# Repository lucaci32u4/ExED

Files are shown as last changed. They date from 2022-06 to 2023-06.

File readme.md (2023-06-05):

# Extended Digital Electronics laboratory

This laboratory is intended to be used as teaching material for the 6th Digital Electronics laboratory in the Faculty of Computer Science, Politehnica University of Bucharest.

This laboratory material presents the functioning of a shift register, a ring counter and a phase-locked loop. The following applications can be built:

 * A semaphore-like appliance using a ring counter
 * A clock divider
 * Phase-locked loop used to correct the pulse width of a fixed-frequency input signal
 * Clock multiplier bult using the phase-locked loop and clock divider
 * Linear feedback shift register - a random number generator using the shift register and XOR gate

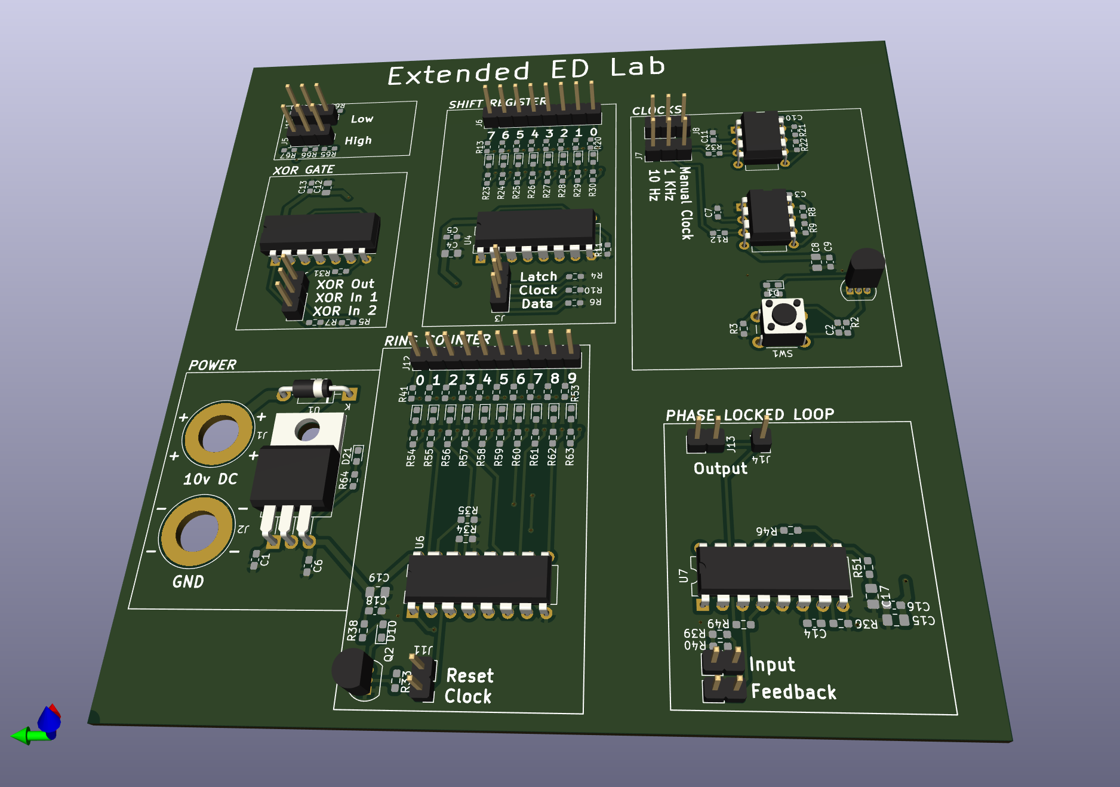
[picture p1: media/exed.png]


## Version v0.1

A batch of 10 boards v0.01 were built. Seven of them were populated and tested in field, while three were kept for archieval purposes.



After teaching the extended laboratory to two groups, the following observations can be made:

 * Replace the XOR gate with a XNOR gate to eliminate the need to seed the LFSR. A XNOR gate would allow it to be self-seeding.
 * There are missing traces near the shift registers that need to be drawn. This issue was fixed by hand using wire on the first batch
 * Remove R36 to allow a much more dynamic range for the PLL.
 * Add LED to all clock inputs to allow better observation of the circuit.
 * Add reverse-polarity protection.

These flaws are planned to be fixed in version v0.2.

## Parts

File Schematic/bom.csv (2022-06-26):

Id | Designator | Package | Quantity | Designation | Supplier and ref
1 | R60,R58,R28,R64,R56,R55,R30,R38,R24,R57,R26,R54,R59,R61,R27,R63,R29,R25,R62,R23,R1 | R_0603_1608Metric_Pad0.98x0.95mm_HandSolder | 21 | 330 | 2861870
2 | D22 | D_DO-41_SOD81_P10.16mm_Horizontal | 1 | 1N4001 | 1458986
3 | J11 | PinHeader_1x02_P2.54mm_Vertical | 1 | CounterControl
4 | U6 | DIP-16_W7.62mm | 1 | 4017 | 3006265
5 | R2,R33 | R_0603_1608Metric_Pad0.98x0.95mm_HandSolder | 2 | 1k | 9233385
6 | U1 | TO-220-3_Horizontal_TabDown | 1 | LM7805_TO220 | 9666095
7 | D4,D11,D5,D17,D2,D7,D13,D16,D1,D10,D18,D9,D8,D14,D19,D3,D15,D12,D6,D21,D20 | LED_0603_1608Metric_Pad1.05x0.95mm_HandSolder | 21 | LED | 2687486
8 | C17,C19,C4,C12,C15,C8 | C_0805_2012Metric_Pad1.18x1.45mm_HandSolder | 6 | 100n | 1414615
9 | U4 | DIP-16_W7.62mm | 1 | 74HC595 | 3120865
10 | J4 | PinHeader_1x03_P2.54mm_Vertical | 1 | XOR
11 | J7,J8 | PinHeader_1x03_P2.54mm_Vertical | 2 | Clocks
12 | R12,R32,R49,R31,R65,R16,R53,R18,R17,R42,R43,R52,R47,R68,R13,R41,R48,R66,R45,R14,R20,R15,R67,R50,R70,R44,R19,R69 | R_0603_1608Metric_Pad0.98x0.95mm_HandSolder | 28 | 100 | 9233253
13 | J3 | PinHeader_1x03_P2.54mm_Vertical | 1 | ShiftInput
14 | C13,C6,C1,C9,C11,C5,C16,C18,C2 | CP_Radial_D4.0mm_P2.00mm | 9 | 1u | 9452524 | changed to 0603 code 1658868
15 | U7 | DIP-16_W7.62mm | 1 | 4046 | 3123331
16 | U5,U2 | DIP-8_W7.62mm | 2 | NE555P | 3006909
17 | J12 | PinHeader_1x10_P2.54mm_Vertical | 1 | CounterOutput
18 | Q1,Q2 | TO-92_Inline | 2 | PN2222A | 1700711
19 | J14 | PinHeader_1x01_P2.54mm_Vertical | 1 | PLLOutput
20 | J15 | PinHeader_1x03_P2.54mm_Vertical | 1 | LogicLow
21 | J2 | Banana_Jack_1Pin | 1 | BananaMinus
22 | J1 | Banana_Jack_1Pin | 1 | BananaPlus
23 | J6 | PinHeader_1x08_P2.54mm_Vertical | 1 | ShiftOutput
24 | R51,R11,R6,R4,R7,R34,R40,R35,R39,R5,R10 | R_0603_1608Metric_Pad0.98x0.95mm_HandSolder | 11 | 10k | 2008360
25 | J10,J9 | PinHeader_1x02_P2.54mm_Vertical | 2 | PLLDivider
26 | C7,C3,C10 | C_1206_3216Metric_Pad1.33x1.80mm_HandSolder | 3 | 10n | 491202 | changed to 0603 code 722236
27 | J5 | PinHeader_1x03_P2.54mm_Vertical | 1 | LogicHigh
28 | SW1 | SW_PUSH_6mm | 1 | Manual
29 | U3 | DIP-14_W7.62mm | 1 | 74LS00 | 3120419
30 | J13 | PinHeader_1x02_P2.54mm_Vertical | 1 | PLLOutput
31 | R9,R22,R8,R21 | R_0603_1608Metric_Pad0.98x0.95mm_HandSolder | 4 | 47k | 1652881
32 | R46,R36 | R_0603_1608Metric_Pad0.98x0.95mm_HandSolder | 2 | 100k | 9233628
33 | R37 | R_0603_1608Metric_Pad0.98x0.95mm_HandSolder | 1 | 10M | 2446549
34 | C14 | C_0603_1608Metric_Pad1.08x0.95mm_HandSolder | 1 | 1nF | 1740627
35 | R3 | R_0603_1608Metric_Pad0.98x0.95mm_HandSolder | 1 | 500 |  | // TODO: replace with 330 ohm

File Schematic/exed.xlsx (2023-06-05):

Id | Designator | Footprint | Quantity | Designation | Supplier and ref
1 | R60,R58,R28,R64,R56,R55,R30,R38,R24,R57,R26,R54,R59,R61,R27,R63,R29,R1,R25,R62,R23 | R_0603_1608Metric_Pad0.98x0.95mm_HandSolder | 21 | 330
2 | D22 | D_DO-41_SOD81_P10.16mm_Horizontal | 1 | 1N4001
3 | J11 | PinHeader_1x02_P2.54mm_Vertical | 1 | CounterControl
4 | U6 | DIP-16_W7.62mm | 1 | 4017
5 | R2,R33 | R_0603_1608Metric_Pad0.98x0.95mm_HandSolder | 2 | 1k
6 | U1 | TO-220-3_Horizontal_TabDown | 1 | LM7805_TO220
7 | D4,D11,D5,D17,D2,D7,D13,D16,D1,D10,D18,D9,D8,D14,D19,D3,D15,D12,D6,D21,D20 | LED_0603_1608Metric_Pad1.05x0.95mm_HandSolder | 21 | LED
8 | C17,C19,C4,C12,C15,C8 | C_0805_2012Metric_Pad1.18x1.45mm_HandSolder | 6 | 100n
9 | U4 | DIP-16_W7.62mm | 1 | 74HC595
10 | J4 | PinHeader_1x03_P2.54mm_Vertical | 1 | XOR
11 | J7,J8 | PinHeader_1x03_P2.54mm_Vertical | 2 | Clocks
12 | R12,R32,R49,R31,R65,R16,R53,R18,R17,R42,R43,R52,R47,R68,R13,R41,R48,R66,R45,R14,R20,R15,R67,R50,R70,R44,R19,R69 | R_0603_1608Metric_Pad0.98x0.95mm_HandSolder | 28 | 100
13 | J3 | PinHeader_1x03_P2.54mm_Vertical | 1 | ShiftInput
14 | C13,C6,C1,C11,C5,C16,C18,C2,C9 | C_0603_1608Metric_Pad1.08x0.95mm_HandSolder | 9 | 1u
15 | U7 | DIP-16_W7.62mm | 1 | 4046
16 | U5,U2 | DIP-8_W7.62mm | 2 | NE555P
17 | J12 | PinHeader_1x10_P2.54mm_Vertical | 1 | CounterOutput
18 | Q1,Q2 | TO-92_Inline | 2 | PN2222A
19 | J14 | PinHeader_1x01_P2.54mm_Vertical | 1 | PLLOutput
20 | J15 | PinHeader_1x03_P2.54mm_Vertical | 1 | LogicLow
21 | J2 | Banana_Jack_1Pin | 1 | BananaMinus
22 | J1 | Banana_Jack_1Pin | 1 | BananaPlus
23 | J6 | PinHeader_1x08_P2.54mm_Vertical | 1 | ShiftOutput
24 | R51,R11,R6,R4,R7,R34,R40,R35,R39,R5,R10 | R_0603_1608Metric_Pad0.98x0.95mm_HandSolder | 11 | 10k
25 | J10,J9 | PinHeader_1x02_P2.54mm_Vertical | 2 | PLLDivider
26 | C7,C3,C10 | C_0603_1608Metric_Pad1.08x0.95mm_HandSolder | 3 | 10n
27 | J5 | PinHeader_1x03_P2.54mm_Vertical | 1 | LogicHigh
28 | SW1 | SW_PUSH_6mm | 1 | Manual
29 | U3 | DIP-14_W7.62mm | 1 | 74LS00
30 | J13 | PinHeader_1x02_P2.54mm_Vertical | 1 | PLLOutput
31 | R9,R22,R8,R21 | R_0603_1608Metric_Pad0.98x0.95mm_HandSolder | 4 | 47k
32 | R46,R36 | R_0603_1608Metric_Pad0.98x0.95mm_HandSolder | 2 | 100k
33 | R37 | R_0603_1608Metric_Pad0.98x0.95mm_HandSolder | 1 | 10M
34 | C14 | C_0603_1608Metric_Pad1.08x0.95mm_HandSolder | 1 | 1nF
35 | R3 | R_0603_1608Metric_Pad0.98x0.95mm_HandSolder | 1 | 500

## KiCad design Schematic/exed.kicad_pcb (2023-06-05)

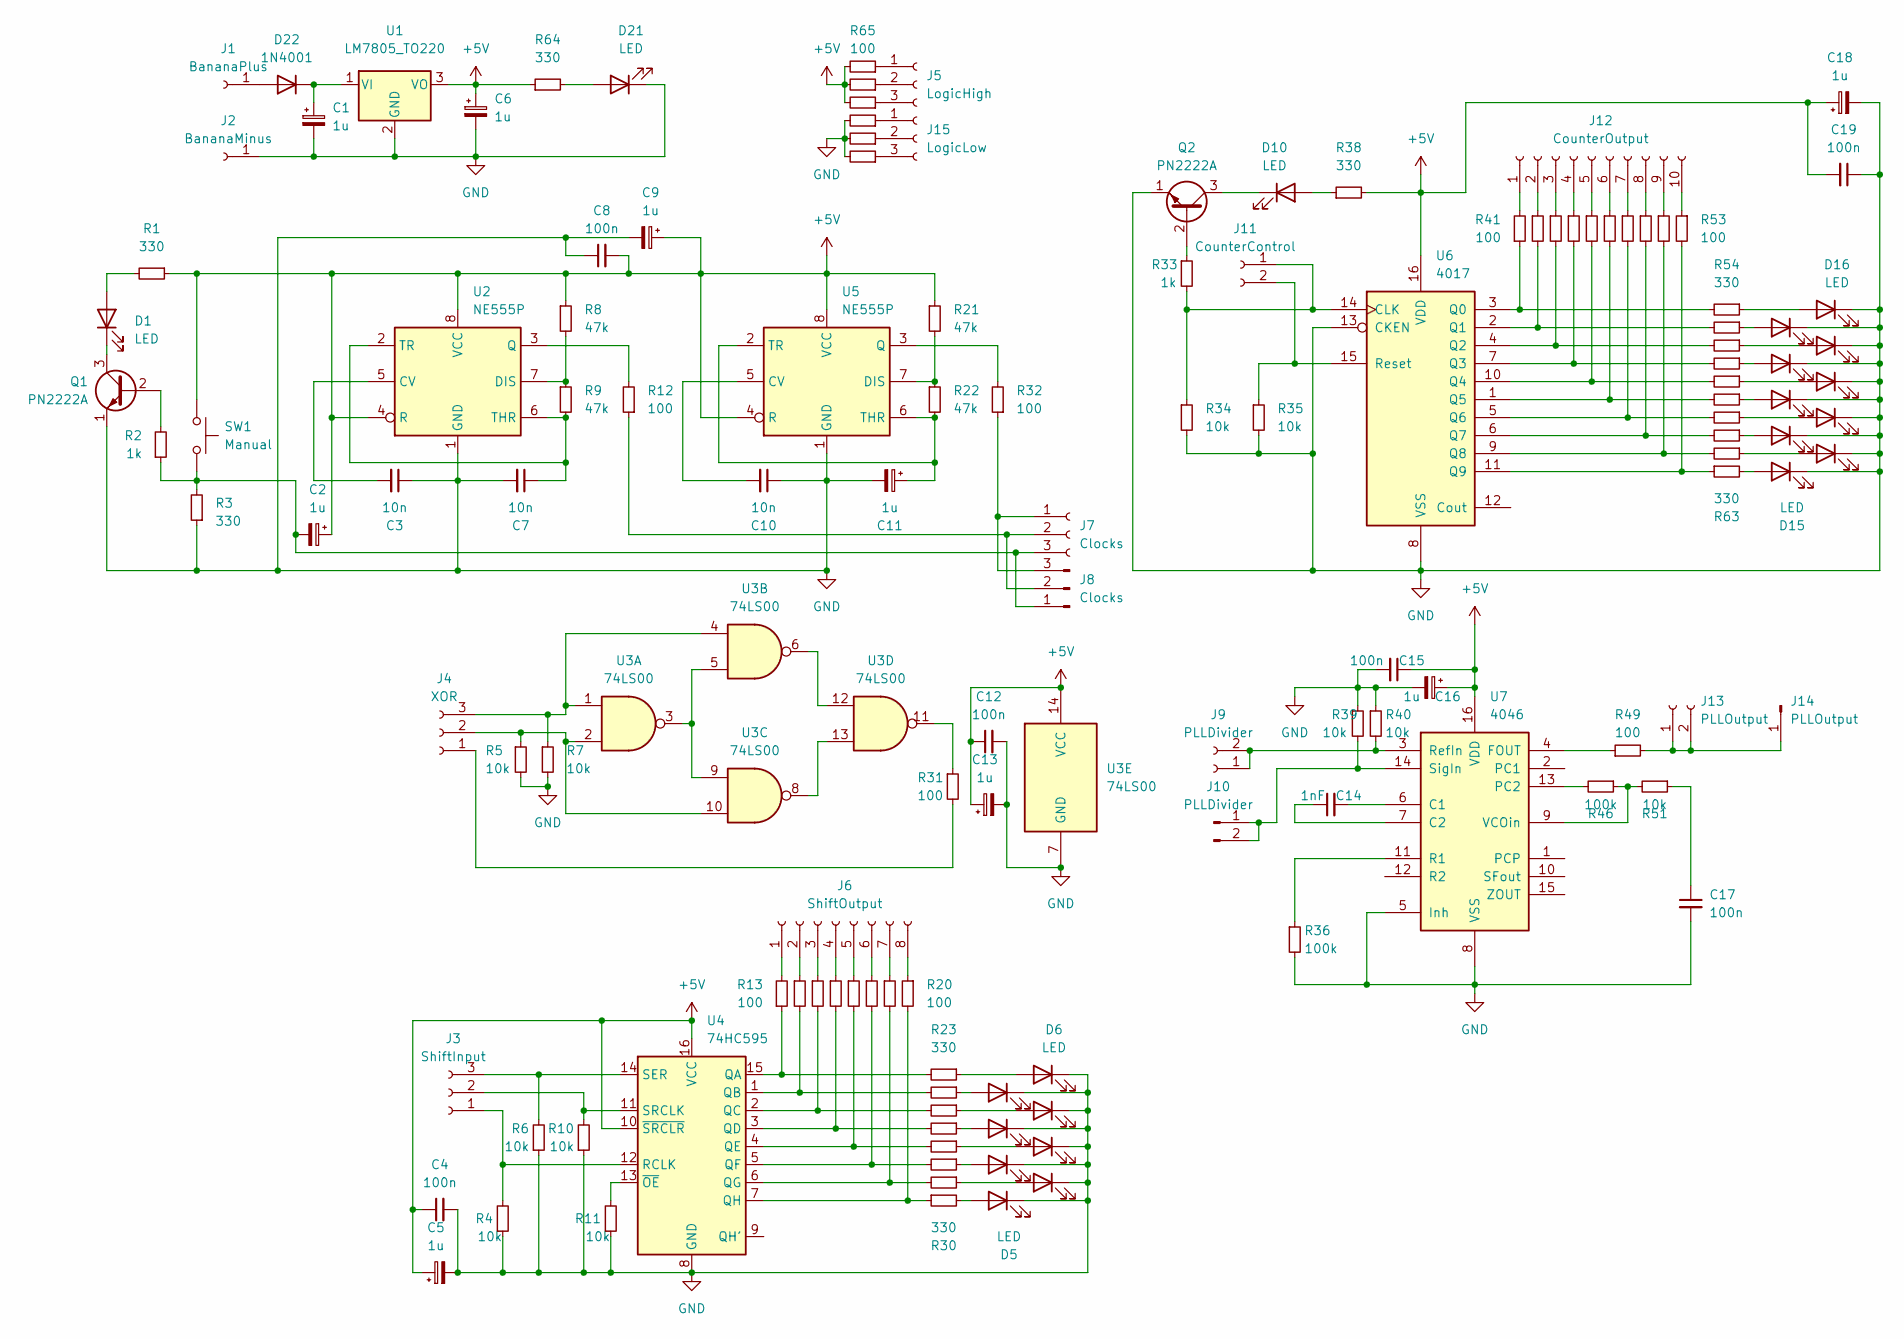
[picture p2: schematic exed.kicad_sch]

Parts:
C1, C2, C5, C6, C9, C11, C13, C16, C18: 1u; C_0603_1608Metric_Pad1.08x0.95mm_HandSolder
C3, C7, C10: 10n; C_0603_1608Metric_Pad1.08x0.95mm_HandSolder
C4, C8, C12, C15, C17, C19: 100n; C_0805_2012Metric_Pad1.18x1.45mm_HandSolder
C14: 1nF; C_0603_1608Metric_Pad1.08x0.95mm_HandSolder
D1, D2, D3, D4, D5, D6, D7, D8, D9, D10, D11, D12, D13, D14, D15, D16, D17, D18, D19, D20, D21: LED; LED_0603_1608Metric_Pad1.05x0.95mm_HandSolder
D22: 1N4001; D_DO-41_SOD81_P10.16mm_Horizontal
J1: BananaPlus; Banana_Jack_1Pin
J2: BananaMinus; Banana_Jack_1Pin
J3: ShiftInput; PinHeader_1x03_P2.54mm_Vertical
J4: XOR; PinHeader_1x03_P2.54mm_Vertical
J5: LogicHigh; PinHeader_1x03_P2.54mm_Vertical
J6: ShiftOutput; PinHeader_1x08_P2.54mm_Vertical
J7, J8: Clocks; PinHeader_1x03_P2.54mm_Vertical
J9, J10: PLLDivider; PinHeader_1x02_P2.54mm_Vertical
J11: CounterControl; PinHeader_1x02_P2.54mm_Vertical
J12: CounterOutput; PinHeader_1x10_P2.54mm_Vertical
J13: PLLOutput; PinHeader_1x02_P2.54mm_Vertical
J14: PLLOutput; PinHeader_1x01_P2.54mm_Vertical
J15: LogicLow; PinHeader_1x03_P2.54mm_Vertical
Q1, Q2: PN2222A; TO-92_Inline
R1, R3, R23, R24, R25, R26, R27, R28, R29, R30, R38, R54, R55, R56, R57, R58, R59, R60, R61, R62, R63, R64: 330; R_0603_1608Metric_Pad0.98x0.95mm_HandSolder
R2, R33: 1k; R_0603_1608Metric_Pad0.98x0.95mm_HandSolder
R4, R5, R6, R7, R10, R11, R34, R35, R39, R40, R51: 10k; R_0603_1608Metric_Pad0.98x0.95mm_HandSolder
R8, R9, R21, R22: 47k; R_0603_1608Metric_Pad0.98x0.95mm_HandSolder
R12, R13, R14, R15, R16, R17, R18, R19, R20, R31, R32, R41, R42, R43, R44, R45, R47, R48, R49, R50, R52, R53, R65, R66, R67, R68, R69, R70: 100; R_0603_1608Metric_Pad0.98x0.95mm_HandSolder
R36, R46: 100k; R_0603_1608Metric_Pad0.98x0.95mm_HandSolder
SW1: Manual; SW_PUSH_6mm
U1: LM7805_TO220; TO-220-3_Horizontal_TabDown
U2, U5: NE555P; DIP-8_W7.62mm
U3: 74LS00; DIP-14_W7.62mm
U4: 74HC595; DIP-16_W7.62mm
U6: 4017; DIP-16_W7.62mm
U7: 4046; DIP-16_W7.62mm

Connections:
+5V: C2.1, C4.1, C5.1, C6.1, C8.2, C9.1, C12.1, C13.1, C15.1, C16.1, C18.1, C19.2, R1.1, R8.1, R21.1, R38.2, R64.1, R65.2, R66.2, R67.2, SW1.1, U1.3 (VO), U2.4 (R), U2.8 (VCC), U3.14 (VCC), U4.10 (~SRCLR), U4.16 (VCC), U5.4 (R), U5.8 (VCC), U6.16 (VDD), U7.16 (VDD)
GND: C1.2, C3.1, C4.2, C5.2, C6.2, C7.2, C8.1, C9.2, C10.1, C11.2, C12.2, C13.2, C15.2, C16.2, C17.2, C18.2, C19.1, D2.1 (K), D3.1 (K), D4.1 (K), D5.1 (K), D6.1 (K), D7.1 (K), D8.1 (K), D9.1 (K), D11.1 (K), D12.1 (K), D13.1 (K), D14.1 (K), D15.1 (K), D16.1 (K), D17.1 (K), D18.1 (K), D19.1 (K), D20.1 (K), D21.1 (K), J2.1, Q1.1 (E), Q2.1 (E), R3.1, R4.1, R5.2, R6.1, R7.2, R10.1, R11.1, R34.2, R35.2, R36.2, R39.1, R40.1, R68.2, R69.2, R70.2, U1.2 (GND), U2.1 (GND), U3.7 (GND), U4.8 (GND), U5.1 (GND), U6.8 (VSS), U6.13 (CKEN), U7.5 (Inh), U7.8 (VSS)
unnamed: C17.1, R51.1
unnamed: D1.2 (A), R1.2
unnamed: D1.1 (K), Q1.3 (C)
unnamed: D2.2 (A), R24.1
unnamed: D3.2 (A), R26.1
unnamed: D4.2 (A), R28.1
unnamed: D5.2 (A), R30.2
unnamed: D6.2 (A), R23.1
unnamed: D7.2 (A), R25.1
unnamed: D8.2 (A), R27.1
unnamed: D9.2 (A), R29.1
unnamed: D10.2 (A), R38.1
unnamed: D10.1 (K), Q2.3 (C)
unnamed: D11.2 (A), R55.1
unnamed: D12.2 (A), R57.1
unnamed: D13.2 (A), R59.1
unnamed: D14.2 (A), R61.1
unnamed: D15.2 (A), R63.2
unnamed: D16.2 (A), R54.1
unnamed: D17.2 (A), R56.1
unnamed: D18.2 (A), R58.1
unnamed: D19.2 (A), R60.1
unnamed: D20.2 (A), R62.1
unnamed: D21.2 (A), R64.2
unnamed: D22.2 (A), J1.1
unnamed: C1.1, D22.1 (K), U1.1 (VI)
unnamed: J3.1, R4.2, U4.12 (RCLK)
unnamed: J3.2, R10.2, U4.11 (SRCLK)
unnamed: J3.3, R6.2, U4.14 (SER)
unnamed: J4.1, R31.2
unnamed: J4.2, R5.1, U3.2, U3.10
unnamed: J4.3, R7.1, U3.1, U3.4
unnamed: J5.1, R65.1
unnamed: J5.2, R66.1
unnamed: J5.3, R67.1
unnamed: J6.1, R13.2
unnamed: J6.2, R14.1
unnamed: J6.3, R15.1
unnamed: J6.4, R16.1
unnamed: J6.5, R17.1
unnamed: J6.6, R18.1
unnamed: J6.7, R19.1
unnamed: J6.8, R20.1
unnamed: J7.1, J8.3, R32.1
unnamed: J7.2, J8.2, R12.1
unnamed: C2.2, J7.3, J8.1, R2.1, R3.2, SW1.2
unnamed: J9.1, J9.2, R40.2, U7.3 (RefIn)
unnamed: J10.1, J10.2, R39.2, U7.14 (SigIn)
unnamed: J11.1, R33.2, R34.1, U6.14 (CLK)
unnamed: J11.2, R35.1, U6.15 (Reset)
unnamed: J12.1, R41.2
unnamed: J12.2, R42.1
unnamed: J12.3, R43.1
unnamed: J12.4, R44.1
unnamed: J12.5, R45.1
unnamed: J12.6, R47.1
unnamed: J12.7, R48.1
unnamed: J12.8, R50.1
unnamed: J12.9, R52.1
unnamed: J12.10, R53.1
unnamed: J13.1, J13.2, J14.1, R49.2
unnamed: J15.1, R68.1
unnamed: J15.2, R69.1
unnamed: J15.3, R70.1
unnamed: Q1.2 (B), R2.2
unnamed: Q2.2 (B), R33.1
unnamed: R31.1, U3.11
unnamed: C3.2, U2.5 (CV)
unnamed: R8.2, R9.1, U2.7 (DIS)
unnamed: R12.2, U2.3 (Q)
unnamed: C7.1, R9.2, U2.2 (TR), U2.6 (THR)
unnamed: U3.3, U3.5, U3.9
unnamed: U3.6, U3.12
unnamed: U3.8, U3.13
unnamed: R13.1, R23.2, U4.15 (QA)
unnamed: R14.2, R24.2, U4.1 (QB)
unnamed: R15.2, R25.2, U4.2 (QC)
unnamed: R16.2, R26.2, U4.3 (QD)
unnamed: R17.2, R27.2, U4.4 (QE)
unnamed: R18.2, R28.2, U4.5 (QF)
unnamed: R19.2, R29.2, U4.6 (QG)
unnamed: R20.2, R30.1, U4.7 (QH)
unnamed: R11.2, U4.13 (~OE)
unnamed: C10.2, U5.5 (CV)
unnamed: R21.2, R22.1, U5.7 (DIS)
unnamed: R32.2, U5.3 (Q)
unnamed: C11.1, R22.2, U5.2 (TR), U5.6 (THR)
unnamed: R41.1, R54.2, U6.3 (Q0)
unnamed: R42.2, R55.2, U6.2 (Q1)
unnamed: R43.2, R56.2, U6.4 (Q2)
unnamed: R44.2, R57.2, U6.7 (Q3)
unnamed: R45.2, R58.2, U6.10 (Q4)
unnamed: R47.2, R59.2, U6.1 (Q5)
unnamed: R48.2, R60.2, U6.5 (Q6)
unnamed: R50.2, R61.2, U6.6 (Q7)
unnamed: R52.2, R62.2, U6.9 (Q8)
unnamed: R53.2, R63.1, U6.11 (Q9)
unnamed: C14.2, U7.6 (C1)
unnamed: C14.1, U7.7 (C2)
unnamed: R49.1, U7.4 (FOUT)
unnamed: R46.2, U7.13 (PC2)
unnamed: R36.1, U7.11 (R1)
unnamed: R46.1, R51.2, U7.9 (VCOin)

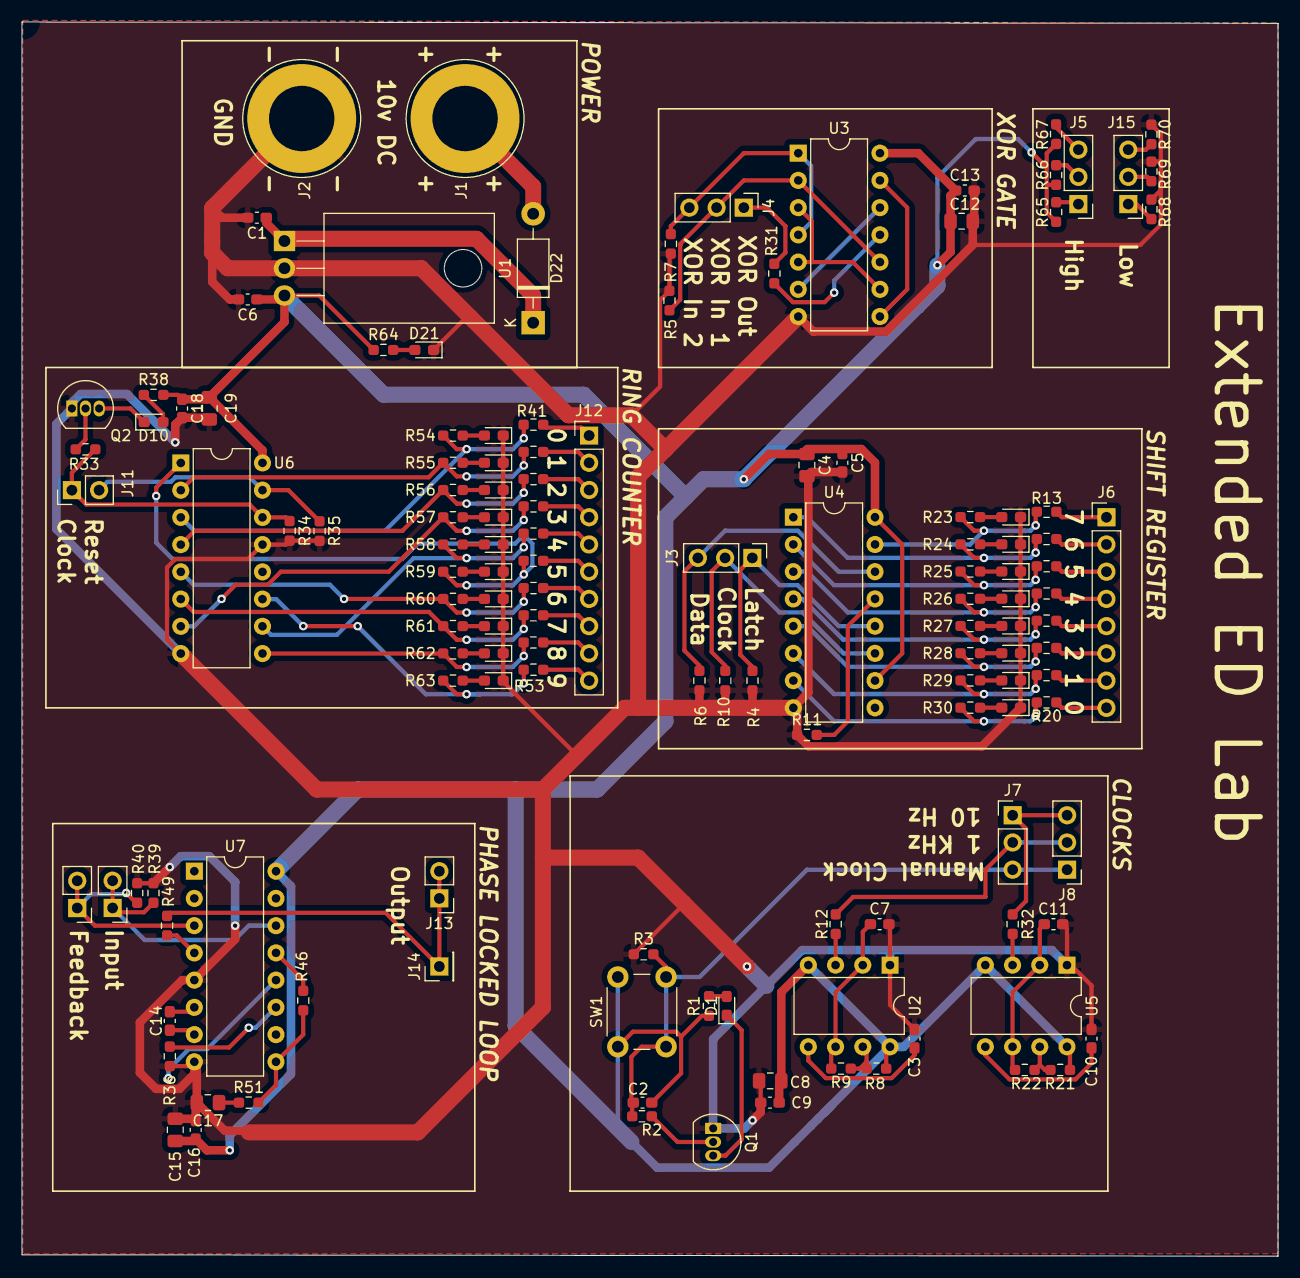
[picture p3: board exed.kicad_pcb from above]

Board: 2 copper layers, 117.2 x 115.1 mm, 135 parts (0 on the bottom side), 105 nets.

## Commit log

2022-06-23 Add schematic prototype and pcb
    [bom.csv, exed.kicad_pcb, exed.kicad_sch]
2022-06-26 Changed footprint of electrolytic to smd 0603
    [bom.csv, exed.kicad_pcb, exed.kicad_sch]
2022-06-27 Added logo and bumped version
    [bom-outdated.csv, exed.kicad_pcb]
2023-06-05 Final version v0.1
    [exed-B_Cu.gbr, exed-B_Mask.gbr, exed-B_Paste.gbr, exed-B_Silkscreen.gbr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]

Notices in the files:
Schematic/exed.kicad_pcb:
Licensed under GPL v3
